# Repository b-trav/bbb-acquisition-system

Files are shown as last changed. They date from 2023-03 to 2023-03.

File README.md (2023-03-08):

# BEAGLEBONE BLACK ACQUISITION SYSTEM

__IMPORTANT: This project was last updated in 2017, so many commands and links are likely to be out of date.__

## Introduction

This project will show you how to create an 8 channel 24-bit 130 kSPS 
data acquisition system using a Beaglebone Black, four ADS1271 
Evaluation modules and a few other electronic bits and pieces.

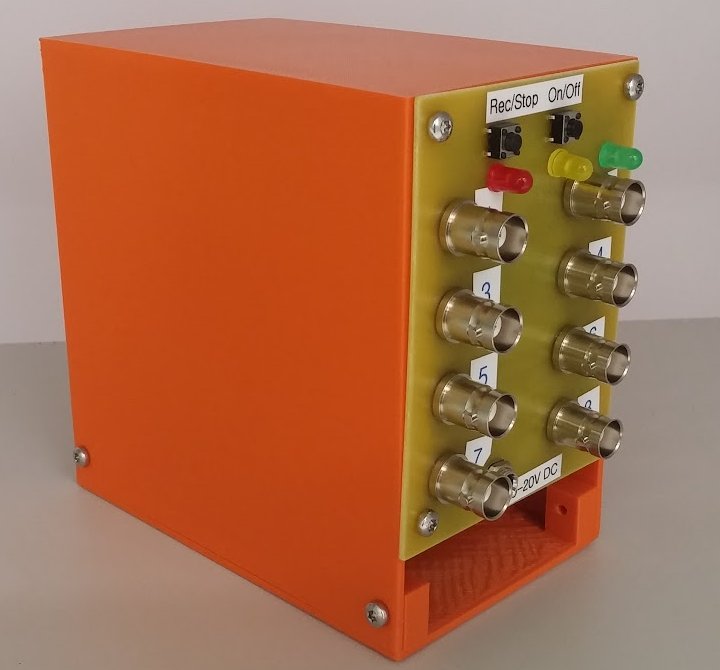
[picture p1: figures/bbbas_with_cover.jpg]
BBB Acquisition System with cover The BBB Acquisition System


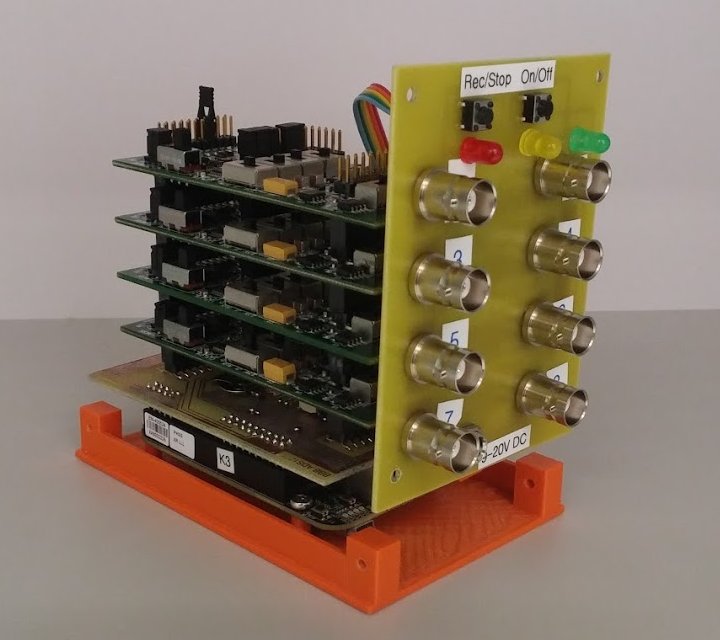
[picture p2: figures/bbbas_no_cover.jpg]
BBB Acquisition System without cover Inside the BBB Acquisition System


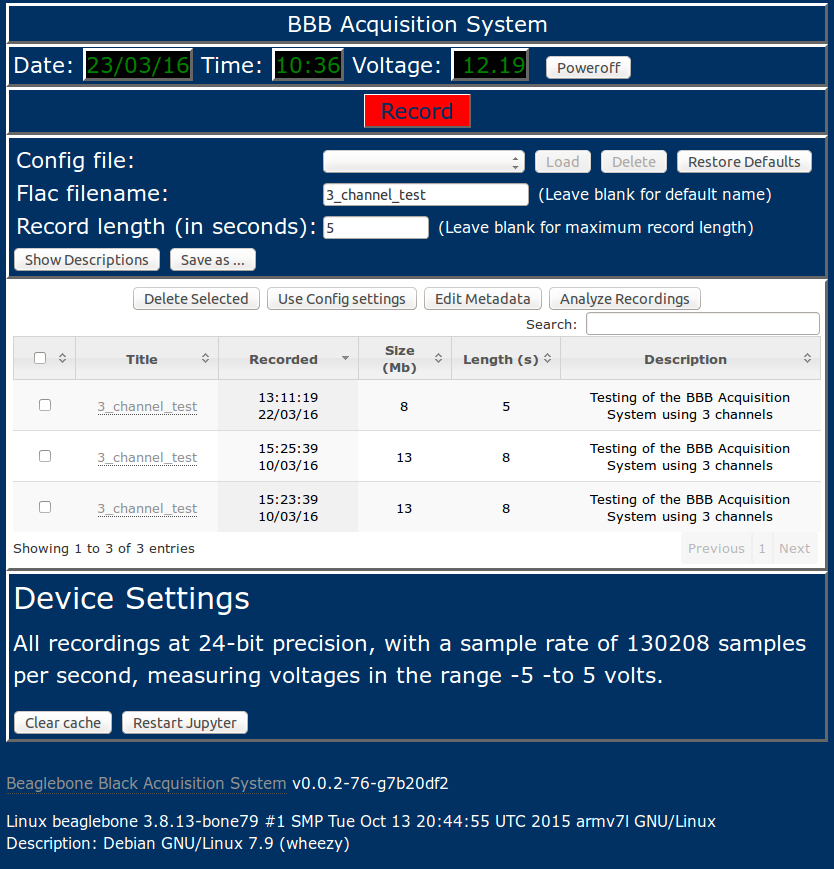
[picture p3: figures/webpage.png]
BBB Acquisition System webpage GUI interface of the BBB Acquisition System


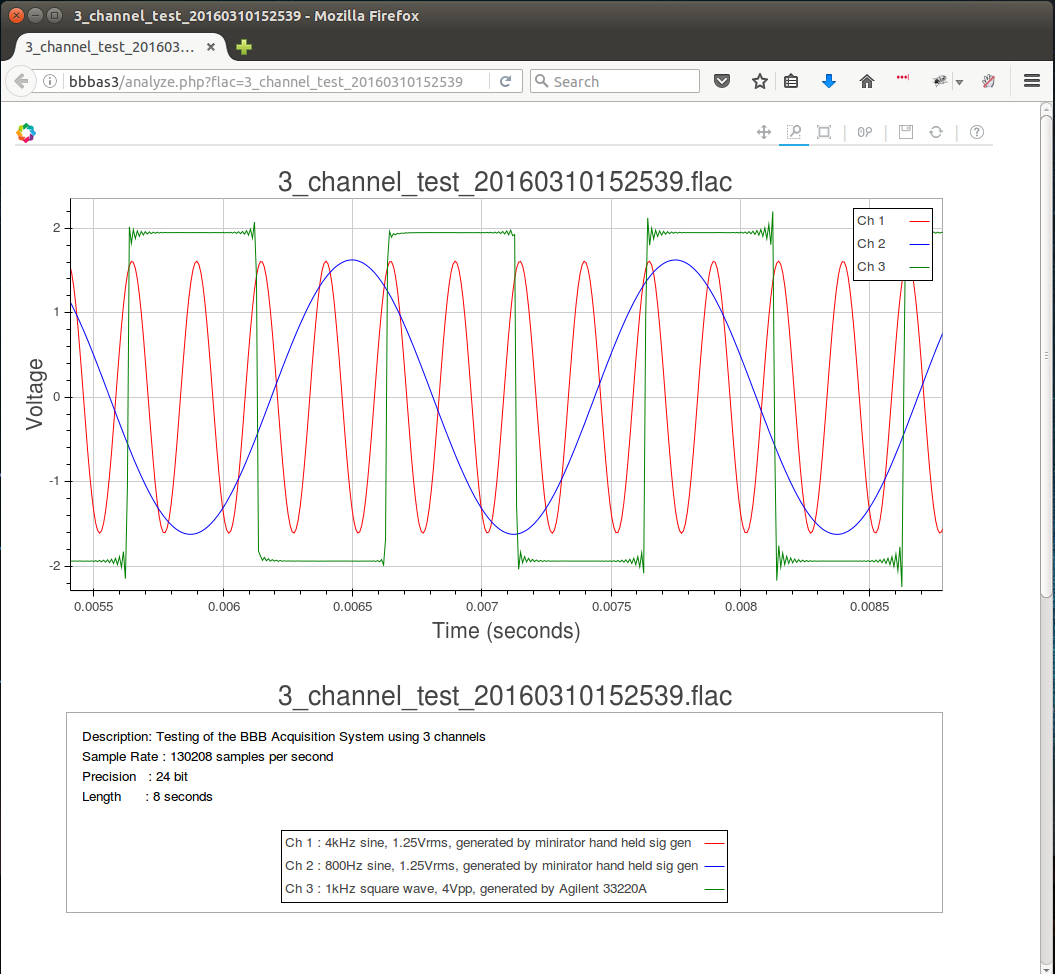
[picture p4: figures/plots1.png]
BBB Acquisition System Analysis Analysis of acquired data


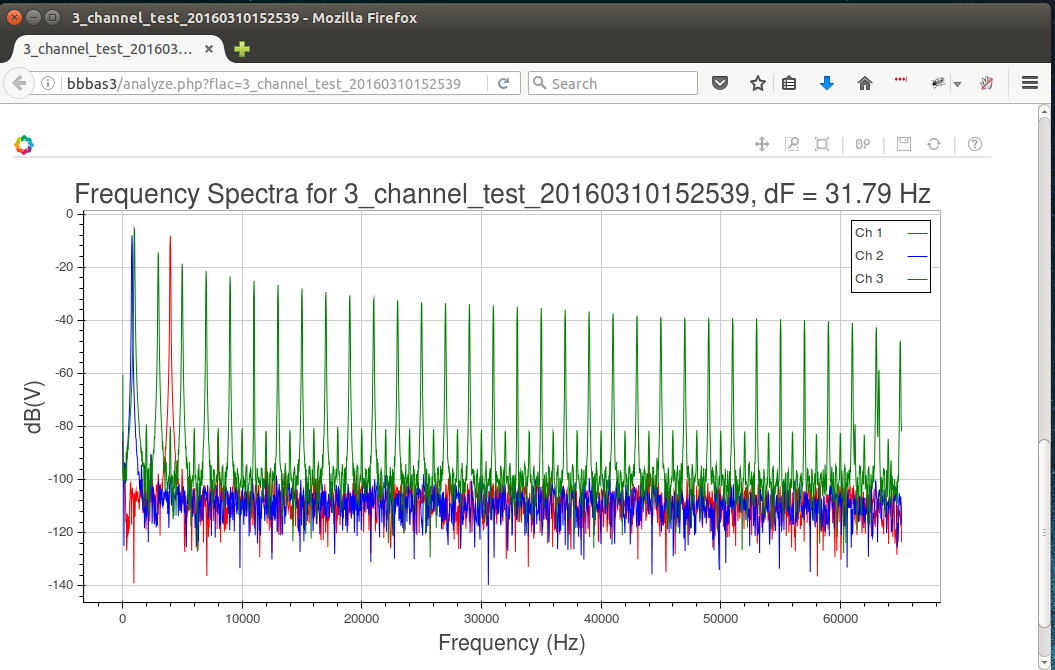
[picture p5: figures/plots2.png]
BBB Acquisition System Analysis Spectral analysis of acquired data


The aim of this project is to give people access to a reliable, 
high-precision data acquisition system which runs at a respectable 
sample rate without having to shell out tens of thousands of dollars.

## Client-side App

The acquisition system can be controlled with any browser, however, to check on the
progress of a recording, or look at the third octave levels of an input, it is necessary
to run a python script on the computer used to access the BBBAS.

To use the client-side app, you need to install python, as well as numpy and bokeh.
So far, the client-side app has only been tested in linux.
The client side app is run using the command
```
BBBASDIR=~/bbb-acquisition-system
bokeh serve --unused-session-lifetime 10 --port 5006 $BBBASDIR/source/third_octave_local.py $BBBASDIR/source/record_progress.py
``` 
This assumes that you have cloned the bbb-acquisition-system repository into
your home directory.

## Bill of Materials

| Product | (Approx.) Price<sup>1</sup> (US$) |
|---------|----------------------------------:|
| [Beaglebone Black]                                          |  $55 |
| [ADS1271EVM] ( 4 @ $49 )                                    | $196 |
| [12V 2A DC Power Supply]<sup>2</sup>                        |   $4 |
| [2Gb microSD card]<sup>3</sup>                              |   $2 |
| [larger microSD card]<sup>4</sup>                           |   $4 |
| [BBB_ADS1271 Cape](#Cape)                                   |  $80 |
| [BBB ADS1271 Front Panel](#FrontPanel)                      |  $30 |
| [Wifi dongle] (optional)                                    |  $12 |
| __Case (optional)__ 
| [Base](#Base) (27 cm<sup>3</sup> of plastic)                |  $10 |
| [Cover](#Cover) (91 cm<sup>3</sup> of plastic)              |  $25 |
| __TOTAL__                                               | __$418__ |

[Beaglebone Black]:http://beagleboard.org/BLACK
[ADS1271EVM]: http://www.ti.com/tool/ads1271evm
[12V 2A DC Power Supply]: http://www.ebay.com/sch/12v+2a+power+supply
[2Gb microSD card]: http://www.ebay.com/sch/2Gb+micro+SD+card
[larger microSD card]: http://www.ebay.com/sch/micro+SD+card
[Wifi dongle]: https://www.adafruit.com/products/814
__Footnotes__:
 
<sup>1</sup>Some components will need to be purchased in quantities 
greater than those required by a single acquisition system, leading to 
a larger over-all cost for the creation of a single unit.

<sup>2</sup>The device will run with any supply voltage between 10 and 
20 volts.

<sup>3</sup>For storing the Linux Debian operating system flasher 
(Can be larger than 2Gb).

<sup>4</sup>For storing the acquired data.

## Software installation procedure

* Download the following compressed flasher image of the debian operating system 
  for the beaglebone black. 
  * [kernel: 3.8.13-bone79 Debian Wheezy image](https://rcn-ee.com/rootfs/bb.org/release/2015-11-03/console/BBB-eMMC-flasher-debian-7.9-console-armhf-2015-11-03-2gb.img.xz)

  > ### Background
  > 
  > There are a heap of different kernel versions of debian available 
  > to download,
  > thanks to the good work of [RobertCNelson](https://github.com/RobertCNelson).
  > These images can be found on the [Embedded Linux Wiki](http://elinux.org/Beagleboard:BeagleBoneBlack_Debian).
  > 
  > I am far from an expert in the world of linux or embedded systems, 
  > but as I understand it, there are two main distinctions with the 
  > kernels.
  > There are kernels 8.13.x which have good support for the 
  > capemanager, but are now rather old, and
  > then there are newer kernels which have better reliability with 
  > regard to wifi etc, but do not *yet* provide good support for adding 
  > capes or using the PRUs.
  > 
  > I have attempted to create an ADS1271 cape which works with 
  > newer kernels, but I have run into some issues. If you are adventurous,
  > you can try:
  > * [kernel: 4.1.16-ti-rt-r44 Debian Jessie image](https://rcn-ee.com/rootfs/bb.org/testing/2016-01-31/console/BBB-eMMC-flasher-debian-8.3-console-armhf-2016-01-31-2gb.img.xz)
  > 
  > CURRENT BUGS: 
  >   * Boot freezes for several minutes when wifi dongle is attached
  >   * Boot freezes for several minutes when PRU is enabled

* Copy this image onto a 2Gb microSD card (this is the minimum size – a 
  larger microSD card will work fine)

  * **Linux** :
  Follow [these instructions](http://www.ev3dev.org/docs/tutorials/writing-sd-card-image-linux-command-line/)

  * **Windows** :
  Follow [these instructions](https://learn.adafruit.com/beaglebone-black-installing-operating-systems/windows)

  * **Mac** :
  Follow [these instructions](https://learn.adafruit.com/beaglebone-black-installing-operating-systems/mac-os-x)

* Eject and insert the SD card into the BBB and power it up (you may need to hold down the SD card
  button on the BBB). 
  Wait for the image to be flashed to the emmc (takes a few minutes) while it is processing, the blues leds should be sweeping back and forth. On conclusion all the blue leds should be on (or wait another minute or so and the device should have powered itself down). 

* Remove the microSD card from the BBB, and save it in case you need to start the installation procedure again, or create another device. 

* **IMPORTANT!!!** LABEL the microSD card CLEARLY, as inserting this into a BBB and powering the device will wipe the eMMC on the beaglebone black.

* Insert a blank (fat32 formatted) microSD card into the BBB. 

* Power up the BBB by connecting the BBB to a computer via mini-USB. 

* WAIT a few minutes or so (be patient). NB: Probably best not to have the wifi
  dongle plugged in at this point.

* You should be able to connect to your beaglebone black.

* In order to connect to the beaglebone and get internet access, you need to do the following
on your computer:

  * **Linux** :
  
	Open a terminal, and type:

  ```
  sudo su
  ifconfig -a
  # Find out which connection the BBB is on (generally eth3, eth4, etc)
  # and which connection your internet is using (generally wlan0 etc)
  # in this example, the BBB is on eth5 and my internet is on wlan0
  ifconfig eth5 192.168.7.1
  iptables --table nat --append POSTROUTING --out-interface wlan0 -j MASQUERADE
  iptables --append FORWARD --in-interface eth5 -j ACCEPT
  echo 1 > /proc/sys/net/ipv4/ip_forward
  exit
  ssh debian@192.168.7.2
  ```

  * **Windows** : 
   
	Follow [these instructions](https://learn.adafruit.com/ssh-to-beaglebone-black-over-usb/installing-drivers-windows), and then [these instructions](https://learn.adafruit.com/ssh-to-beaglebone-black-over-usb/ssh-with-windows-and-putty).

  * **Mac** : 
   
	Follow [these instructions](https://learn.adafruit.com/ssh-to-beaglebone-black-over-usb/installing-drivers-mac), and then open a terminal and type:
  
  ```
  ssh debian@192.168.7.2
  ```

* Once you have ssh access to the beaglebone, log in via ssh (the default password is temppwd) and then type:

  ```
  sudo ip route add default via 192.168.7.1
  sudo sh -c "echo 'nameserver 8.8.8.8' >> /etc/resolv.conf"
  sudo apt-get -y update
  sudo apt-get -y install git locales
  sudo dpkg-reconfigure locales
  sudo dpkg-reconfigure tzdata
  sudo sh -c "locale > /etc/locale.conf"
  git clone https://github.com/bbb-acquisition-system
  sudo bbb-acquisition-system/install.sh  2>&1 | tee install-bbb-as-log.txt
  ```
  
  Unfortunately this installation procedure takes a reasonably long time 
  (depending on your internet access speed) 
  because we need to install quite a few applications.
  The main hold-up is a couple of python packages (numpy and jupyter),
  which take roughly 35 minutes and 15 minutes respectively to install.
  This gives a total install time of around an hour. 
  Assuming you've set up your locale and timezone, the only user inputs
  are a root password, and then some wifi info at the very end. 
  So after giving your root password,
  go take a long walk, and come back in around an hour.

* After re-booting the BBB you should be able to access your 
  Beaglebone Black Acquisition System by going
  to the ip address of the BBB using a browser of your choice. 

## Building the boards

The BBB Acquisition System requires two printed computer boards (PCBs) to function correctly.
The [Eagle](http://www.cadsoftusa.com/download-eagle/) schematics and 
boards are contained in the PCBs directory, this directory also contains
a set of gerber files for each board.
These boards can be produced using the PCB production company of your choice, or can be generated
in-house, assuming you have the relevant know-how.

### BBB ADS1271 Cape

This board provides power, a real-time clock and the connections between the BBB and
the ADS1271EVMs. 
[Here](PCBs/BBB_ADS1271_cape_parts.html) is a parts list for this board.
Some of the items can only be purchased in large quantities, such as the surface mounted LEDs.
These are not strictly necessary, so if you do not have access to some surface mounted LEDs,
then these can be omitted.

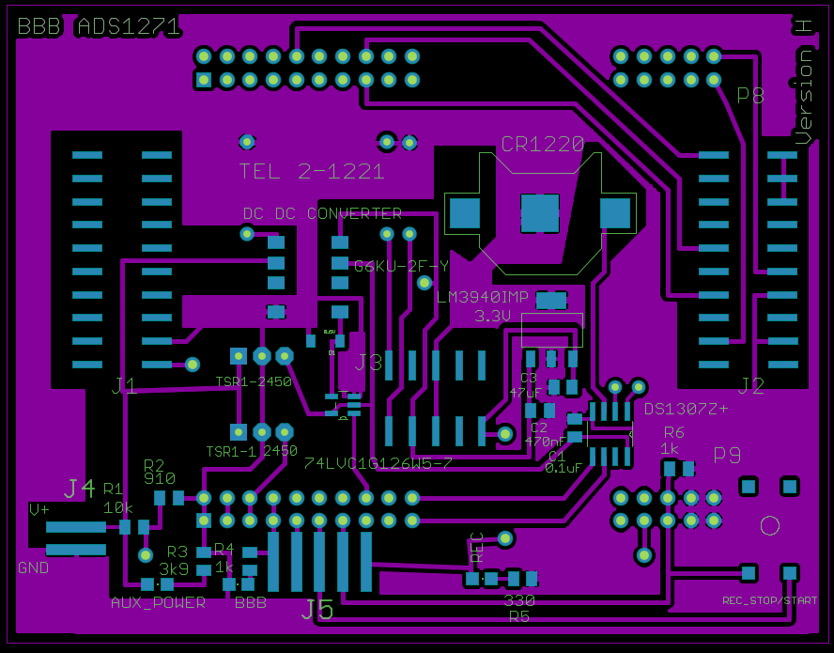
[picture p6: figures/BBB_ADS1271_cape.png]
BBB ADS1271 Cape Board diagram for the BBB ADS1271 Cape


### BBB ADS1271 Front Panel

This board provides the inputs to the system as well as on/off and recording lights and buttons.
[Here](PCBs/BBB_ADS1271_front_panel_parts.html) is a parts list for this board.

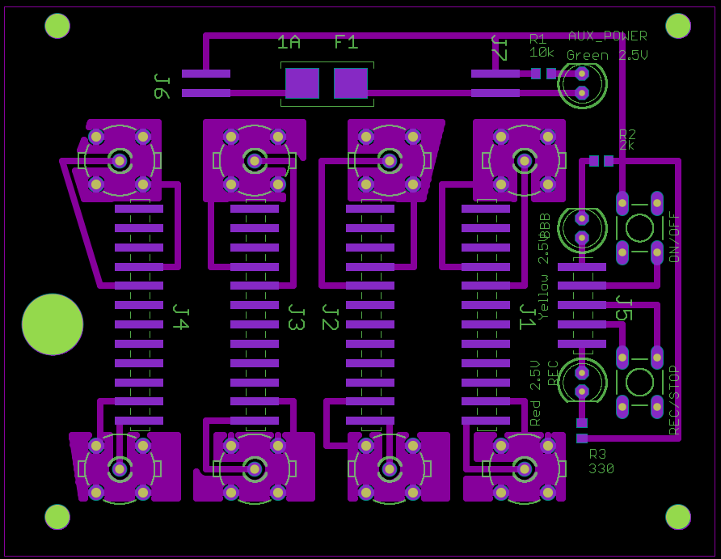
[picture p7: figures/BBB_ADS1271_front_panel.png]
BBB ADS1271 Front Panel Board diagram for the BBB ADS1271 Front Panel


## Building the case

The case for the unit is optional, although highly recommended.
The case directory contains the [blender](https://www.blender.org/) 
and [stl](https://en.wikipedia.org/wiki/STL_%28file_format%29) files for the case.
Once again, if you have access to a 3D printer, you can produce this yourself, otherwise
there are plenty of [3D printing companies](http://3dprintingpricecheck.com/) that you could use.

### Base

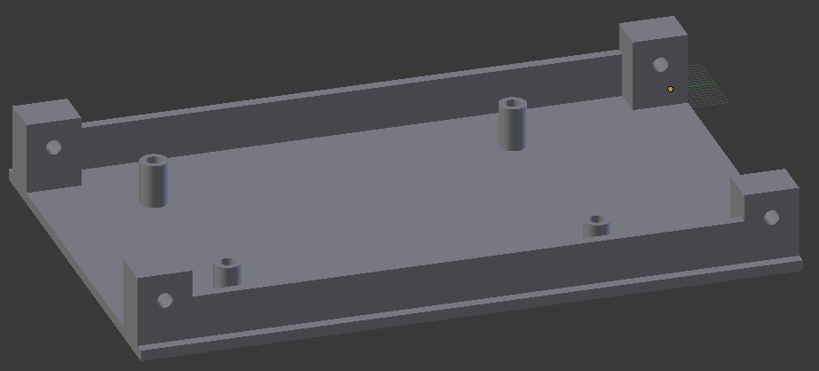
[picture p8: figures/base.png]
BBB Acquisition System Base Base for the BBB Acquisition System


### Cover

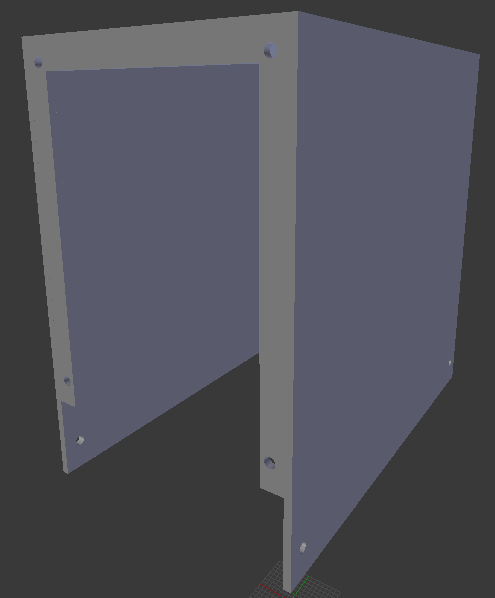
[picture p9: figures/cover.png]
BBB Acquisition System Cover Cover for the BBB Acquisition System


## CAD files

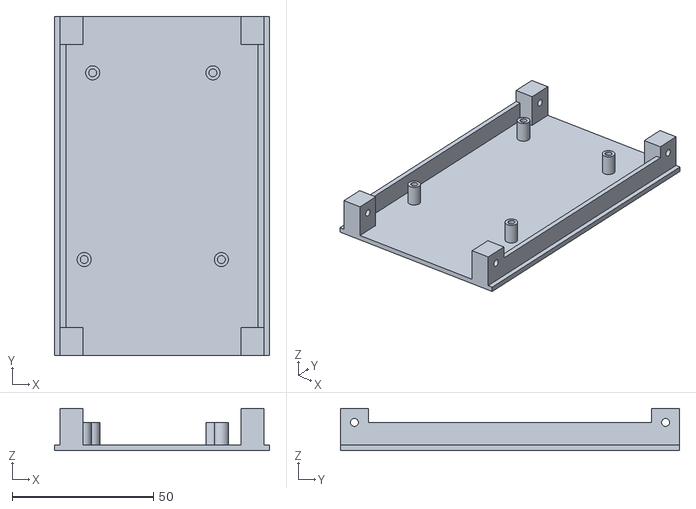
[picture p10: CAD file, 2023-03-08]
case/case_base.stl
76.0 x 120.0 x 15.0

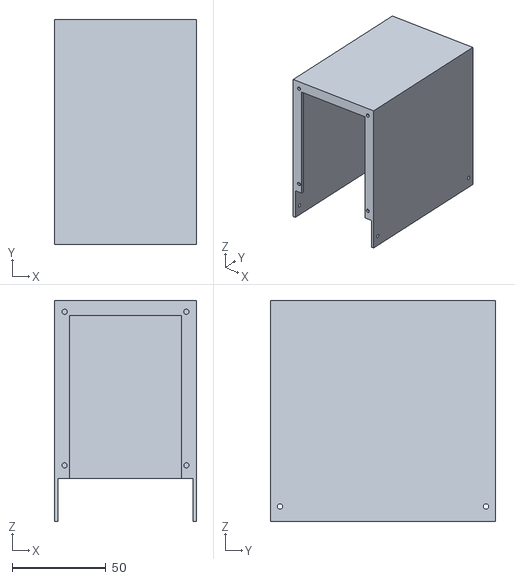
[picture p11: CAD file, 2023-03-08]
case/case_cover.stl
76.0 x 120.0 x 118.0

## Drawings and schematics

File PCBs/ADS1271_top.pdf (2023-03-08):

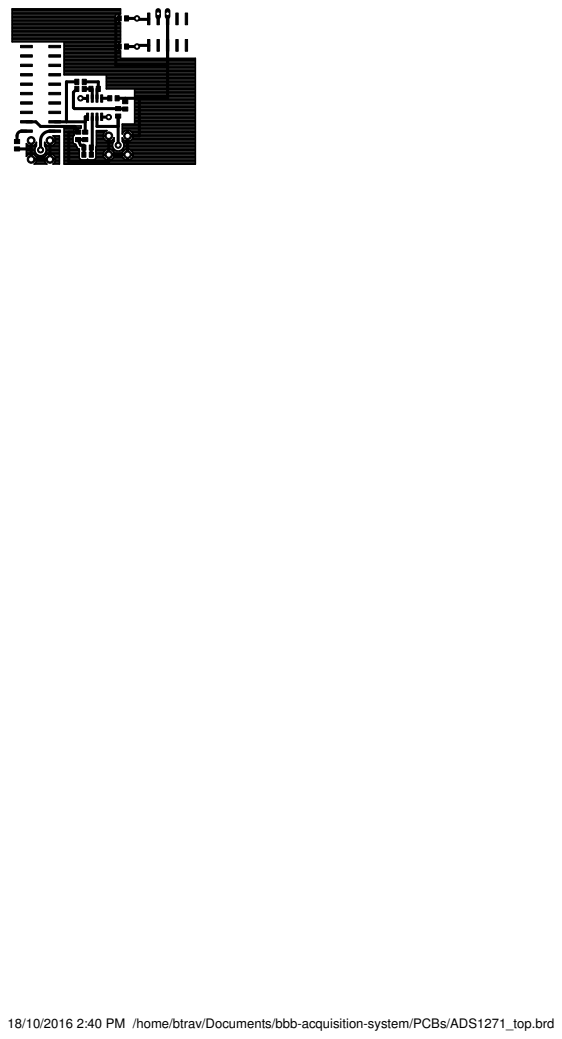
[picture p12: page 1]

18/10/2016 2:40 PM /home/btrav/Documents/bbb-acquisition-system/PCBs/ADS1271_top.brd

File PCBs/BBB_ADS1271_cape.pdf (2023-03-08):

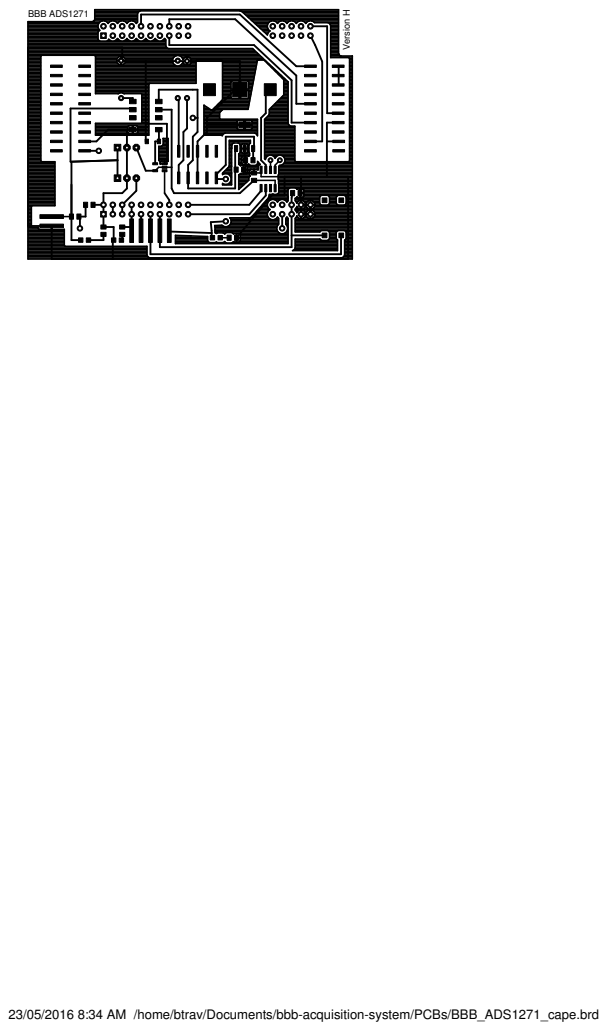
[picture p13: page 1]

23/05/2016 8:34 AM /home/btrav/Documents/bbb-acquisition-system/PCBs/BBB_ADS1271_cape.brd

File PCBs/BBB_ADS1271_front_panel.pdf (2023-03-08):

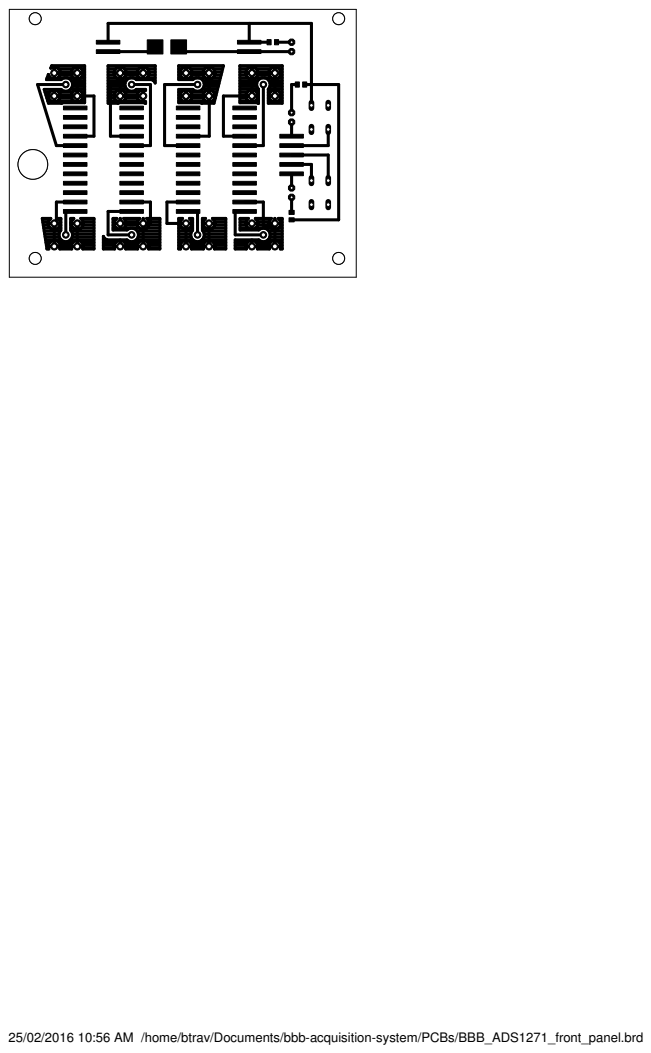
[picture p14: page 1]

25/02/2016 10:56 AM /home/btrav/Documents/bbb-acquisition-system/PCBs/BBB_ADS1271_front_panel.brd

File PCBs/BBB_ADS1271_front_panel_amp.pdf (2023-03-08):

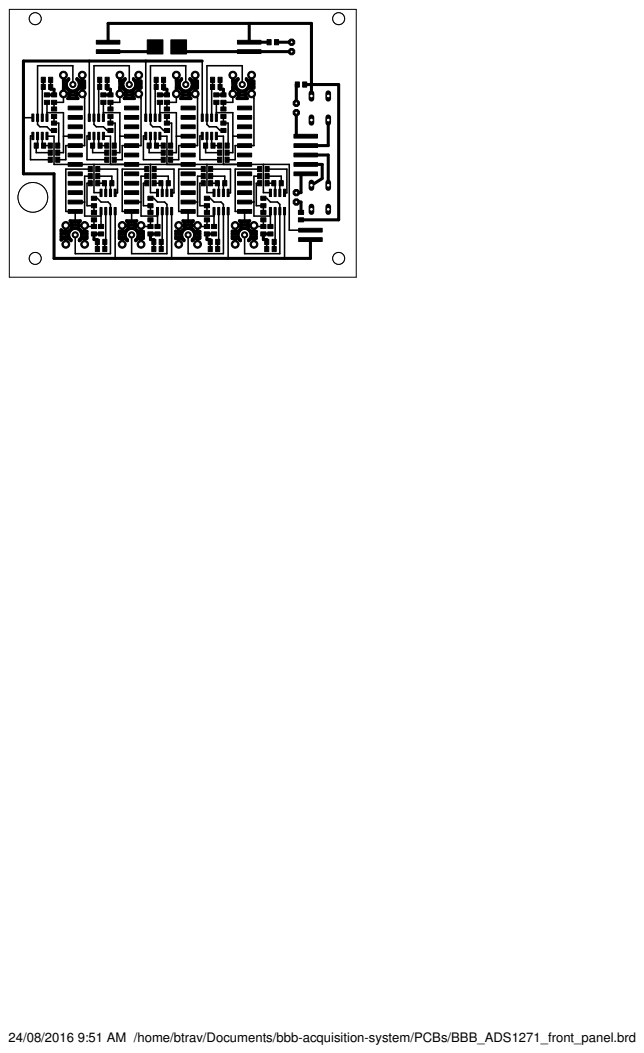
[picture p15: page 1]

24/08/2016 9:51 AM /home/btrav/Documents/bbb-acquisition-system/PCBs/BBB_ADS1271_front_panel.brd

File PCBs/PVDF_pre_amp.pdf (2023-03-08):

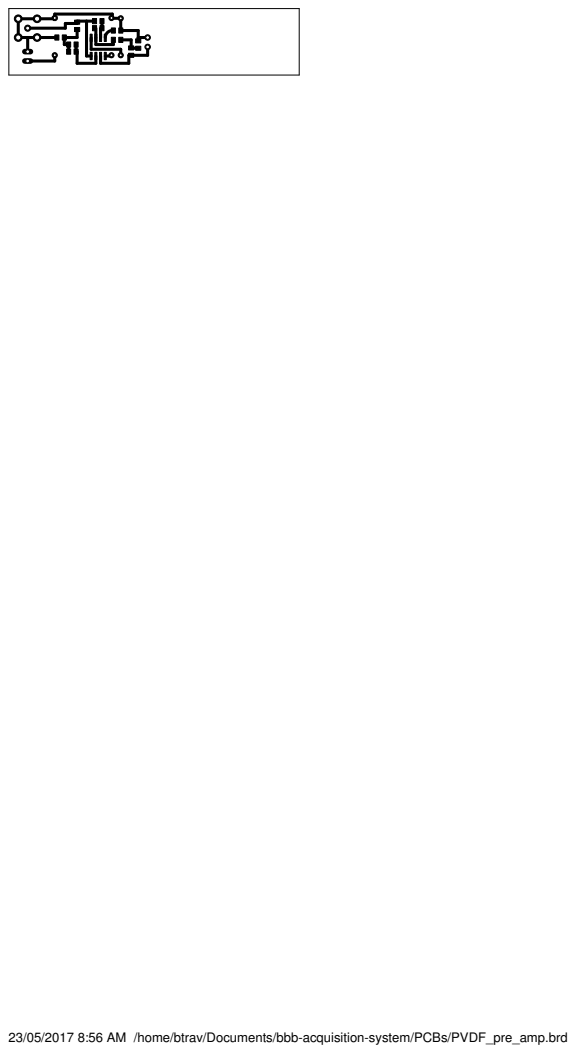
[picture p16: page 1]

23/05/2017 8:56 AM /home/btrav/Documents/bbb-acquisition-system/PCBs/PVDF_pre_amp.brd

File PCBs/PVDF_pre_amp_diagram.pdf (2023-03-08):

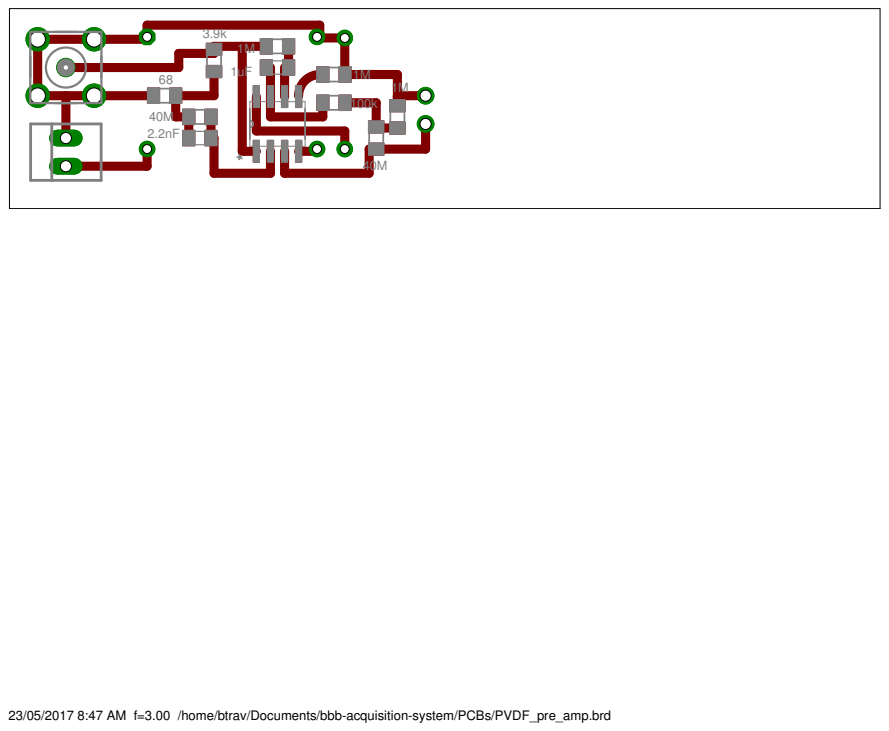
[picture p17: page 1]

23/05/2017 8:47 AM f=3.00 /home/btrav/Documents/bbb-acquisition-system/PCBs/PVDF_pre_amp.brd

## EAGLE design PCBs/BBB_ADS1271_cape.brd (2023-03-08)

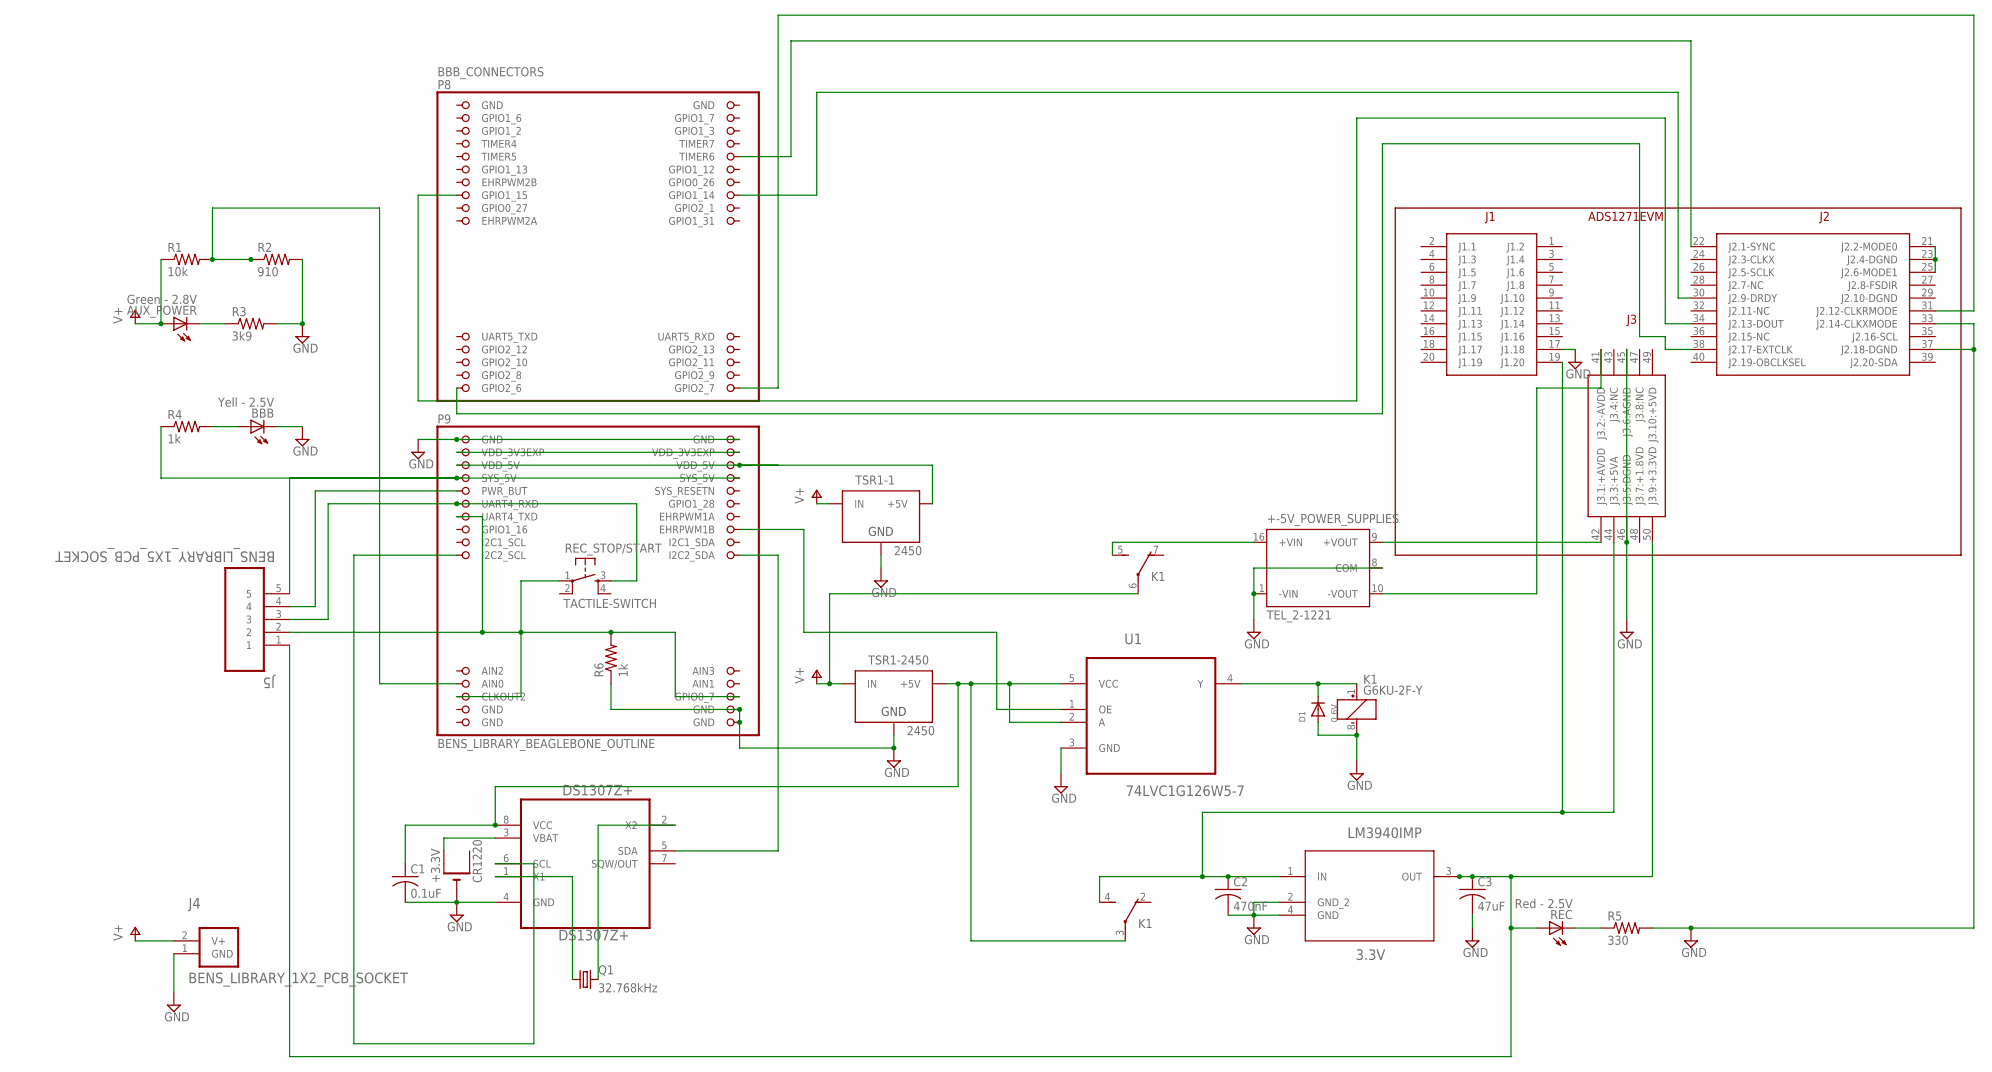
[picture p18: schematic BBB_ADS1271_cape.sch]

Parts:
+-5V_POWER_SUPPLIES: TEL_2-1221; TRACOPOWER2W
ADS1271_CONNECTORS: BENS_LIBRARY_ADS1271EVM
AUX_POWER: Green - 2.8V; CHIPLED_0805
BBB: Yell - 2.5V; CHIPLED_0805
BBB_CONNECTORS: BENS_LIBRARY_BEAGLEBONE_OUTLINE; BENS_LIBRARY_BEAGLEBONE_SHIELD
C1: 0.1uF; C0805K
C2: 470nF; C0805K
C3: 47uF; C0805K
CR1220: +3.3V; ADAFRUIT_CR1220-SMD
D1: 0.6V; SOD-123FL
DS1307Z+: DS1307Z+; MAXIM_BY_ELEMENT14_BATCH_1_SOIC127P600X175-8N
J4: BENS_LIBRARY_1X2_PCB_SOCKET
J5: BENS_LIBRARY_1X5_PCB_SOCKET; BENS_LIBRARY_SAMTEC_SSM-15-L-DV-BE
K1: G6KU-2F-Y
LM3940IMP: 3.3V; NSC_BY_ELEMENT14_BATCH_1.1_SOT230P696X180-4N
Q1: 32.768kHz; TC38H
R1: 10k; ADAFRUIT_R0805
R2: 910; ADAFRUIT_R0805
R3: 3k9; ADAFRUIT_R0805
R4, R6: 1k; ADAFRUIT_R0805
R5: 330; ADAFRUIT_R0805
REC: Red - 2.5V; CHIPLED_0805
REC_STOP/START: TACTILE-SWITCH; 7914G-6MM
TSR1-1, TSR1-2450: 2450; STEELCAVEROBOTICS-POWER_TSR-1
U1: 74LVC1G126W5-7; SOT95P280X145-5N

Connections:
3.3V_BBB_1: BBB_CONNECTORS.57 (UART4_RXD), J5.3, REC_STOP/START.3
3.3V_BBB_2: ADS1271_CONNECTORS.31 (J2.12-CLKRMODE), BBB_CONNECTORS.46 (GPIO2_7)
3.3V_RELAY: ADS1271_CONNECTORS.50 (J3.9:+3.3VD), C3.1, J5.1, LM3940IMP.3 (OUT), REC.A
5V: C1.1, DS1307Z+.8 (VCC), K1.3, TSR1-2450.3 (+5V), U1.2 (A), U1.5 (VCC)
5V_BBB: BBB_CONNECTORS.51 (VDD_5V), BBB_CONNECTORS.52 (VDD_5V), TSR1-1.3 (+5V)
5V_RELAY: ADS1271_CONNECTORS.19 (J1.20), ADS1271_CONNECTORS.44 (J3.3:+5VA), C2.1, K1.4 (S), LM3940IMP.1 (IN)
+5V_OP_AMP: +-5V_POWER_SUPPLIES.9 (+VOUT), ADS1271_CONNECTORS.42 (J3.1:+AVDD)
-5V_OP_AMP: +-5V_POWER_SUPPLIES.10 (-VOUT), ADS1271_CONNECTORS.41 (J3.2:-AVDD)
CLK: ADS1271_CONNECTORS.38 (J2.17-EXTCLK), BBB_CONNECTORS.45 (GPIO2_6)
DGND: ADS1271_CONNECTORS.21 (J2.2-MODE0), ADS1271_CONNECTORS.23 (J2.4-DGND), ADS1271_CONNECTORS.25 (J2.6-MODE1)
DOUT: ADS1271_CONNECTORS.34 (J2.13-DOUT), BBB_CONNECTORS.15 (GPIO1_15)
DRDY: ADS1271_CONNECTORS.30 (J2.9-DRDY), BBB_CONNECTORS.16 (GPIO1_14)
GND: +-5V_POWER_SUPPLIES.1 (-VIN), +-5V_POWER_SUPPLIES.8 (COM), ADS1271_CONNECTORS.17 (J1.18), ADS1271_CONNECTORS.33 (J2.14-CLKXMODE), ADS1271_CONNECTORS.37 (J2.18-DGND), ADS1271_CONNECTORS.45 (J3.6:AGND), ADS1271_CONNECTORS.46 (J3.5:DGND), BBB.C, BBB_CONNECTORS.47 (GND), BBB_CONNECTORS.48 (GND), BBB_CONNECTORS.89 (GND), BBB_CONNECTORS.90 (GND), BBB_CONNECTORS.91 (GND), BBB_CONNECTORS.92 (GND), C1.2, C2.2, C3.2, CR1220.-, D1.A, DS1307Z+.4 (GND), J4.1 (GND), K1.8 (-), LM3940IMP.2 (GND_2), LM3940IMP.4 (GND), R2.2, R3.2, R5.2, R6.1, TSR1-1.2 (GND), TSR1-2450.2 (GND), U1.3 (GND)
unnamed: CR1220.+$2 (+1), DS1307Z+.3 (VBAT)
unnamed: +-5V_POWER_SUPPLIES.16 (+VIN), K1.5 (S)
unnamed: BBB_CONNECTORS.85 (AIN0), R1.2, R2.1
unnamed: BBB_CONNECTORS.66 (I2C2_SDA), DS1307Z+.5 (SDA)
unnamed: BBB_CONNECTORS.65 (I2C2_SCL), DS1307Z+.6 (SCL)
unnamed: DS1307Z+.2 (X2), Q1.2
unnamed: DS1307Z+.1 (X1), Q1.1
unnamed: AUX_POWER.C, R3.1
unnamed: D1.C, K1.1 (+), U1.4 (Y)
unnamed: R5.1, REC.C
unnamed: BBB.A, R4.2
P8.9: BBB_CONNECTORS.62 (EHRPWM1B), U1.1 (OE)
PWR_BUT: BBB_CONNECTORS.55 (PWR_BUT), J5.4
REC_SWITCH: BBB_CONNECTORS.59 (UART4_TXD), BBB_CONNECTORS.87 (CLKOUT2), BBB_CONNECTORS.88 (GPIO0_7), J5.2, R6.2, REC_STOP/START.1
SYNC: ADS1271_CONNECTORS.22 (J2.1-SYNC), BBB_CONNECTORS.10 (TIMER6)
SYS_5V: BBB_CONNECTORS.53 (SYS_5V), BBB_CONNECTORS.54 (SYS_5V), J5.5, R4.1
V+: AUX_POWER.A, J4.2 (V+), K1.6, R1.1, TSR1-1.1 (IN), TSR1-2450.1 (IN)
VDD_3V3EXP: BBB_CONNECTORS.49 (VDD_3V3EXP), BBB_CONNECTORS.50 (VDD_3V3EXP)

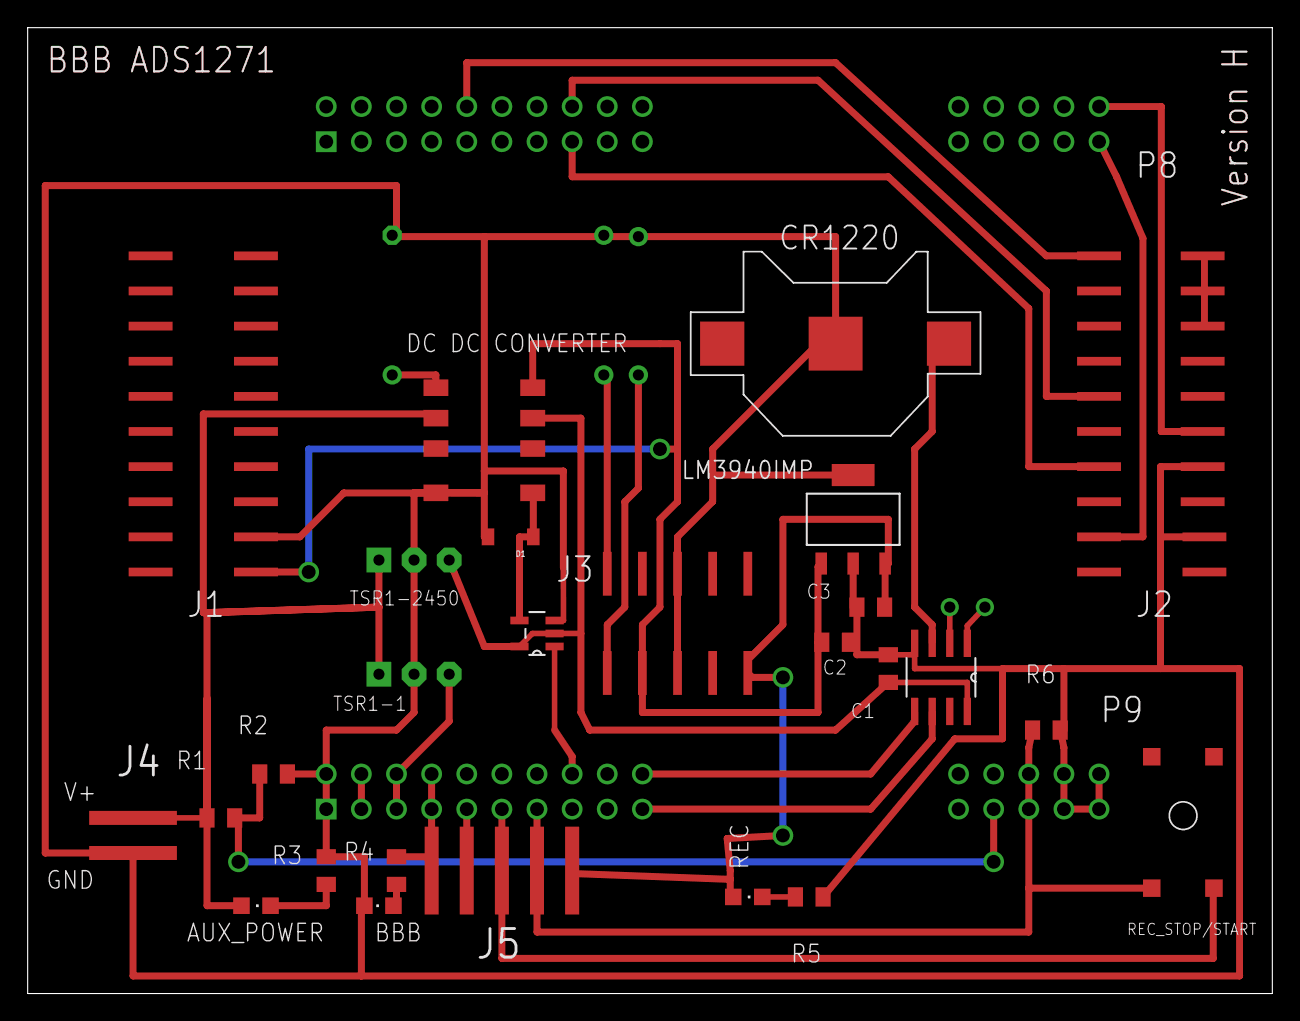
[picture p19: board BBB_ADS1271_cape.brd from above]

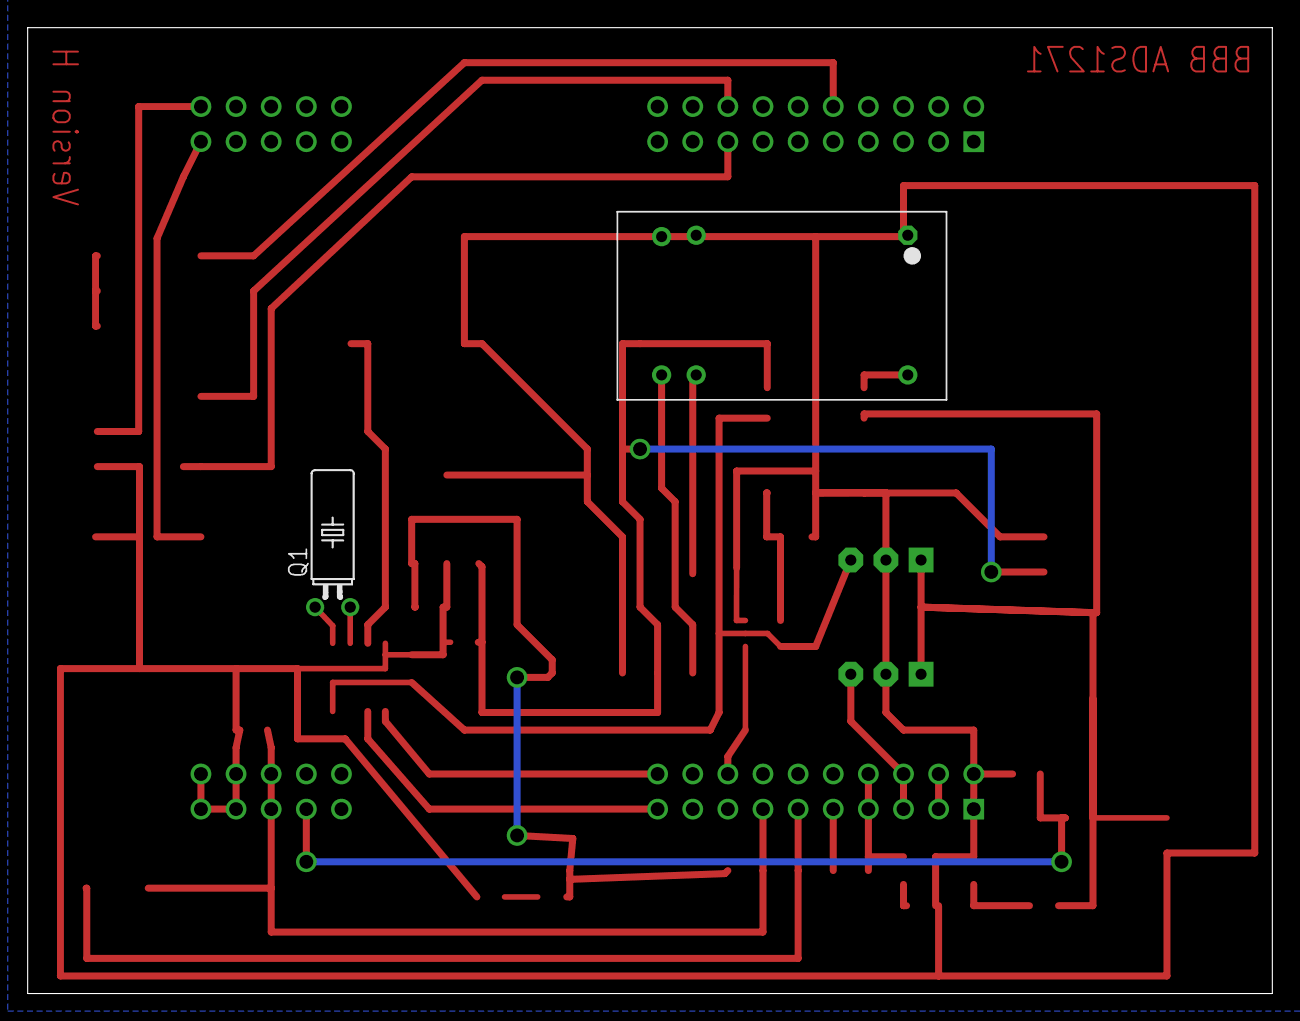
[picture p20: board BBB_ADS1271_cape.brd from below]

Board: 2 copper layers, 90.0 x 69.8 mm, 27 parts (4 on the bottom side), 31 nets.

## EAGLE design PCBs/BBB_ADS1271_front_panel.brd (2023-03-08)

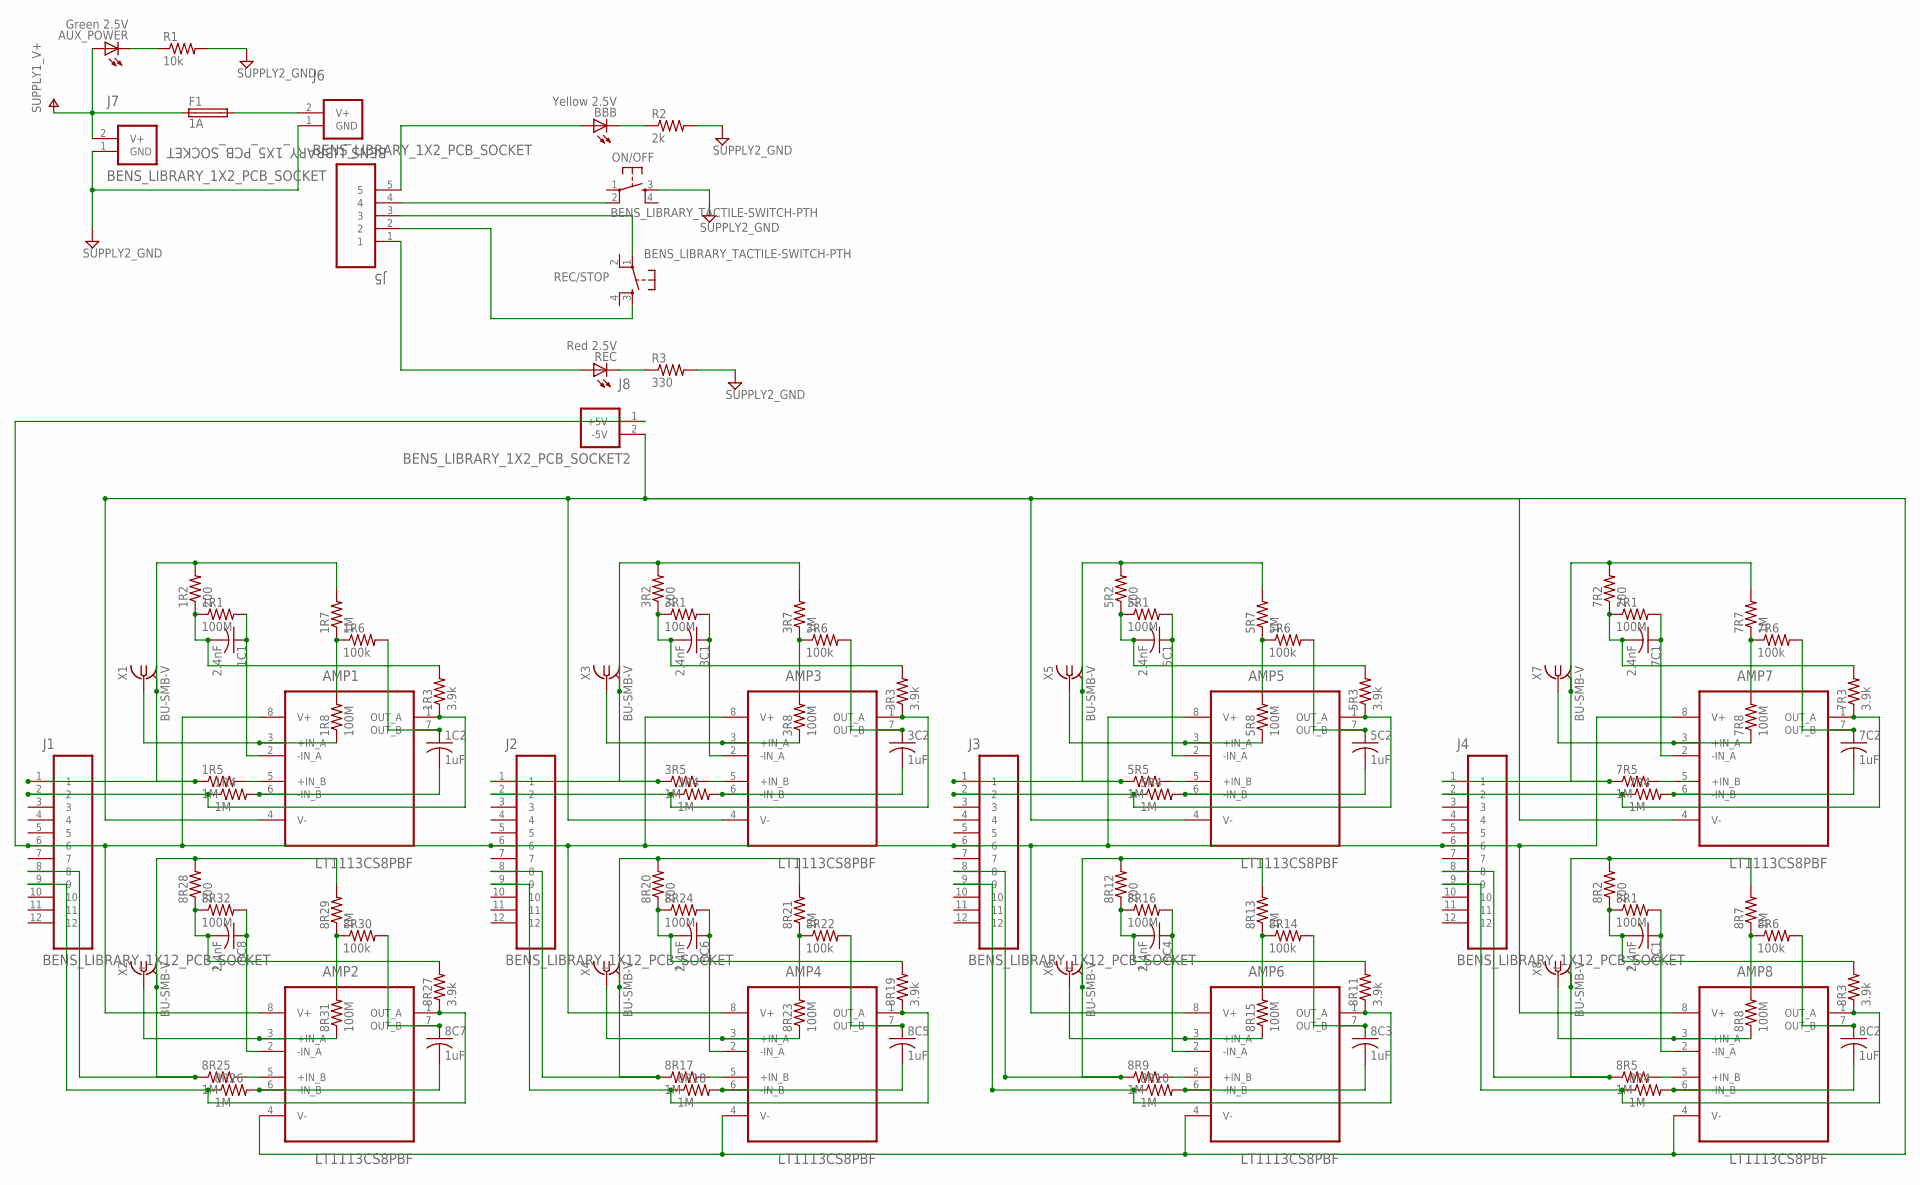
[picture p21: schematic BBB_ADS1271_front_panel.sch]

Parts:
1C1, 3C1, 5C1, 7C1, 8C1, 8C4, 8C6, 8C8: 2.4nF; ADAFRUIT_C0805K
1C2, 3C2, 5C2, 7C2, 8C2, 8C3, 8C5, 8C7: 1uF; ADAFRUIT_C0805K
1R1, 1R8, 3R1, 3R8, 5R1, 5R8, 7R1, 7R8, 8R1, 8R8, 8R15, 8R16, 8R23, 8R24, 8R31, 8R32: 100M; ADAFRUIT_R0805
1R2, 3R2, 5R2, 7R2, 8R2, 8R12, 8R20, 8R28: 200; ADAFRUIT_R0805
1R3, 3R3, 5R3, 7R3, 8R3, 8R11, 8R19, 8R27: 3.9k; ADAFRUIT_R0805
1R4, 1R5, 1R7, 3R4, 3R5, 3R7, 5R4, 5R5, 5R7, 7R4, 7R5, 7R7, 8R4, 8R5, 8R7, 8R9, 8R10, 8R13, 8R17, 8R18, 8R21, 8R25, 8R26, 8R29: 1M; ADAFRUIT_R0805
1R6, 3R6, 5R6, 7R6, 8R6, 8R14, 8R22, 8R30: 100k; ADAFRUIT_R0805
AMP1, AMP2, AMP3, AMP4, AMP5, AMP6, AMP7, AMP8: LT1113CS8PBF; SOIC127P600X175-8N
AUX_POWER: Green 2.5V; ADAFRUIT_LED5MM
BBB: Yellow 2.5V; ADAFRUIT_LED5MM
F1: 1A; LITTLEFUSE_PACKAGE
J1, J2, J3, J4: BENS_LIBRARY_1X12_PCB_SOCKET; BENS_LIBRARY_SAMTEC_SSM-112-L-DV-BE
J5: BENS_LIBRARY_1X5_PCB_SOCKET; BENS_LIBRARY_SAMTEC_SSM-15-L-DV-BE
J6, J7: BENS_LIBRARY_1X2_PCB_SOCKET
J8: BENS_LIBRARY_1X2_PCB_SOCKET2
ON/OFF: BENS_LIBRARY_TACTILE-SWITCH-PTH; BENS_LIBRARY_TAC-SWITCH-PTH
R1: 10k; ADAFRUIT_R0805
R2: 2k; ADAFRUIT_R0805
R3: 330; ADAFRUIT_R0805
REC: Red 2.5V; ADAFRUIT_LED5MM
REC/STOP: BENS_LIBRARY_TACTILE-SWITCH-PTH; BENS_LIBRARY_TAC-SWITCH-PTH
X1, X2, X3, X4, X5, X6, X7, X8: BU-SMB-V

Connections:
1+IN_B: 1R5.2, AMP1.5 (+IN_B)
1-IN_A: 1C1.1, 1R1.2, AMP1.2 (-IN_A)
1-IN_B: 1C2.2, 1R4.2, AMP1.6 (-IN_B)
1OUT_B: 1C2.1, 1R6.2, AMP1.7 (OUT_B)
1W1: 1C1.2, 1R1.1, 1R2.1, 1R3.2
1W2: 1R6.1, 1R7.1, 1R8.2
2+IN_B: 8R25.2, AMP2.5 (+IN_B)
2-IN_A: 8C8.1, 8R32.2, AMP2.2 (-IN_A)
2-IN_B: 8C7.2, 8R26.2, AMP2.6 (-IN_B)
2OUT_B: 8C7.1, 8R30.2, AMP2.7 (OUT_B)
2W1: 8C8.2, 8R27.2, 8R28.1, 8R32.1
2W2: 8R29.1, 8R30.1, 8R31.2
3+IN_B: 3R5.2, AMP3.5 (+IN_B)
3-IN_A: 3C1.1, 3R1.2, AMP3.2 (-IN_A)
3-IN_B: 3C2.2, 3R4.2, AMP3.6 (-IN_B)
3OUT_B: 3C2.1, 3R6.2, AMP3.7 (OUT_B)
3W1: 3C1.2, 3R1.1, 3R2.1, 3R3.2
3W2: 3R6.1, 3R7.1, 3R8.2
4+IN_B: 8R17.2, AMP4.5 (+IN_B)
4-IN_A: 8C6.1, 8R24.2, AMP4.2 (-IN_A)
4-IN_B: 8C5.2, 8R18.2, AMP4.6 (-IN_B)
4OUT_B: 8C5.1, 8R22.2, AMP4.7 (OUT_B)
4W1: 8C6.2, 8R19.2, 8R20.1, 8R24.1
4W2: 8R21.1, 8R22.1, 8R23.2
5+IN_B: 5R5.2, AMP5.5 (+IN_B)
5-IN_A: 5C1.1, 5R1.2, AMP5.2 (-IN_A)
5-IN_B: 5C2.2, 5R4.2, AMP5.6 (-IN_B)
5OUT_B: 5C2.1, 5R6.2, AMP5.7 (OUT_B)
5W1: 5C1.2, 5R1.1, 5R2.1, 5R3.2
5W2: 5R6.1, 5R7.1, 5R8.2
6+IN_B: 8R9.2, AMP6.5 (+IN_B)
6-IN_A: 8C4.1, 8R16.2, AMP6.2 (-IN_A)
6-IN_B: 8C3.2, 8R10.2, AMP6.6 (-IN_B)
6OUT_B: 8C3.1, 8R14.2, AMP6.7 (OUT_B)
6W1: 8C4.2, 8R11.2, 8R12.1, 8R16.1
6W2: 8R13.1, 8R14.1, 8R15.2
7+IN_B: 7R5.2, AMP7.5 (+IN_B)
7-IN_A: 7C1.1, 7R1.2, AMP7.2 (-IN_A)
7-IN_B: 7C2.2, 7R4.2, AMP7.6 (-IN_B)
7OUT_B: 7C2.1, 7R6.2, AMP7.7 (OUT_B)
7W1: 7C1.2, 7R1.1, 7R2.1, 7R3.2
7W2: 7R6.1, 7R7.1, 7R8.2
8+IN_B: 8R5.2, AMP8.5 (+IN_B)
8-IN_A: 8C1.1, 8R1.2, AMP8.2 (-IN_A)
8-IN_B: 8C2.2, 8R4.2, AMP8.6 (-IN_B)
8OUT_B: 8C2.1, 8R6.2, AMP8.7 (OUT_B)
8W1: 8C1.2, 8R1.1, 8R2.1, 8R3.2
8W2: 8R6.1, 8R7.1, 8R8.2
+5V: AMP1.8 (V+), AMP2.8 (V+), AMP3.8 (V+), AMP4.8 (V+), AMP5.8 (V+), AMP6.8 (V+), AMP7.8 (V+), AMP8.8 (V+), J1.6, J2.6, J3.6, J4.6, J8.1 (+5V)
-5V: AMP1.4 (V-), AMP2.4 (V-), AMP3.4 (V-), AMP4.4 (V-), AMP5.4 (V-), AMP6.4 (V-), AMP7.4 (V-), AMP8.4 (V-), J8.2 (-5V)
ADC1_NEG: 1R3.1, 1R4.1, AMP1.1 (OUT_A), J1.2
ADC1_POS: 1R2.2, 1R5.1, 1R7.2, J1.1, X1.2, X1.3 (2), X1.4 (2), X1.5 (2)
ADC2_NEG: 8R26.1, 8R27.1, AMP2.1 (OUT_A), J1.9
ADC2_POS: 8R25.1, 8R28.2, 8R29.2, J1.8, X2.2, X2.3 (2), X2.4 (2), X2.5 (2)
ADC3_NEG: 3R3.1, 3R4.1, AMP3.1 (OUT_A), J2.2
ADC3_POS: 3R2.2, 3R5.1, 3R7.2, J2.1, X3.2, X3.3 (2), X3.4 (2), X3.5 (2)
ADC4_NEG: 8R18.1, 8R19.1, AMP4.1 (OUT_A), J2.9
ADC4_POS: 8R17.1, 8R20.2, 8R21.2, J2.8, X4.2, X4.3 (2), X4.4 (2), X4.5 (2)
ADC5_NEG: 5R3.1, 5R4.1, AMP5.1 (OUT_A), J3.2
ADC5_POS: 5R2.2, 5R5.1, 5R7.2, J3.1, X5.2, X5.3 (2), X5.4 (2), X5.5 (2)
ADC6_NEG: 8R10.1, 8R11.1, AMP6.1 (OUT_A), J3.9
ADC6_POS: 8R9.1, 8R12.2, 8R13.2, J3.8, X6.2, X6.3 (2), X6.4 (2), X6.5 (2)
ADC7_NEG: 7R3.1, 7R4.1, AMP7.1 (OUT_A), J4.2
ADC7_POS: 7R2.2, 7R5.1, 7R7.2, J4.1, X7.2, X7.3 (2), X7.4 (2), X7.5 (2)
ADC8_NEG: 8R3.1, 8R4.1, AMP8.1 (OUT_A), J4.9
ADC8_POS: 8R2.2, 8R5.1, 8R7.2, J4.8, X8.2, X8.3 (2), X8.4 (2), X8.5 (2)
GND: J6.1 (GND), J7.1 (GND), ON/OFF.3, R1.2, R2.2, R3.2
INPUT1_NEG: 1R8.1, AMP1.3 (+IN_A), X1.1
INPUT2_NEG: 8R31.1, AMP2.3 (+IN_A), X2.1
INPUT3_NEG: 3R8.1, AMP3.3 (+IN_A), X3.1
INPUT4_NEG: 8R23.1, AMP4.3 (+IN_A), X4.1
INPUT5_NEG: 5R8.1, AMP5.3 (+IN_A), X5.1
INPUT6_NEG: 8R15.1, AMP6.3 (+IN_A), X6.1
INPUT7_NEG: 7R8.1, AMP7.3 (+IN_A), X7.1
INPUT8_NEG: 8R8.1, AMP8.3 (+IN_A), X8.1
unnamed: BBB.A, J5.5
unnamed: AUX_POWER.K (C), R1.1
unnamed: J5.1, REC.A
unnamed: J5.4, ON/OFF.2
unnamed: J5.3, REC/STOP.1
unnamed: J5.2, REC/STOP.3
unnamed: R3.1, REC.K (C)
unnamed: BBB.K (C), R2.1
V+: AUX_POWER.A, F1.P$1 (1), J7.2 (V+)
V+_FUSED: F1.P$2 (2), J6.2 (V+)

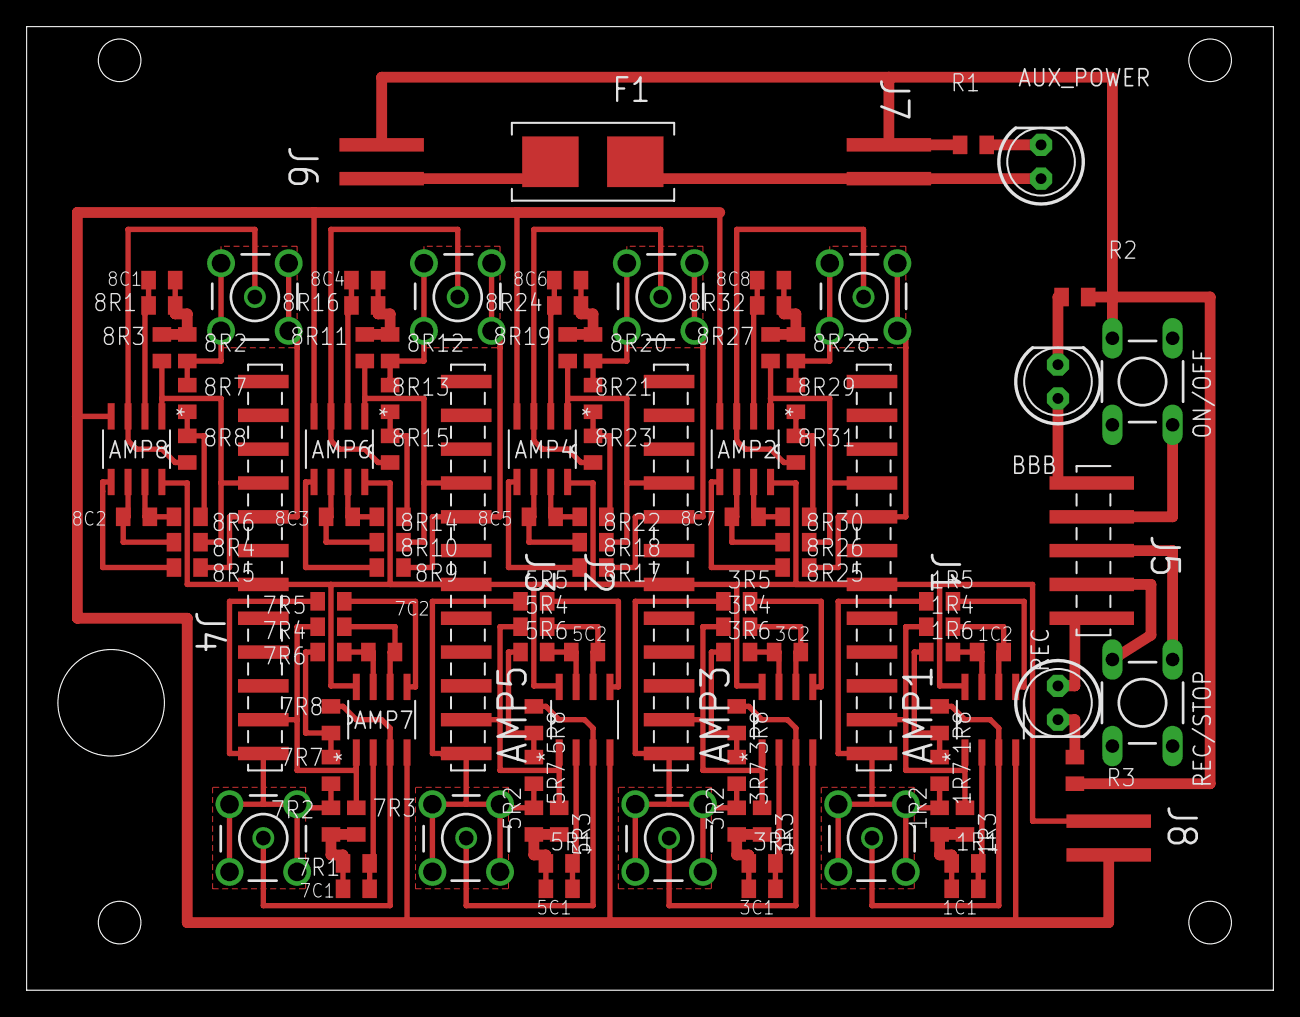
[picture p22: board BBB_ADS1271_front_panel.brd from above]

Board: 2 copper layers, 93.7 x 72.4 mm, 113 parts (0 on the bottom side), 85 nets.

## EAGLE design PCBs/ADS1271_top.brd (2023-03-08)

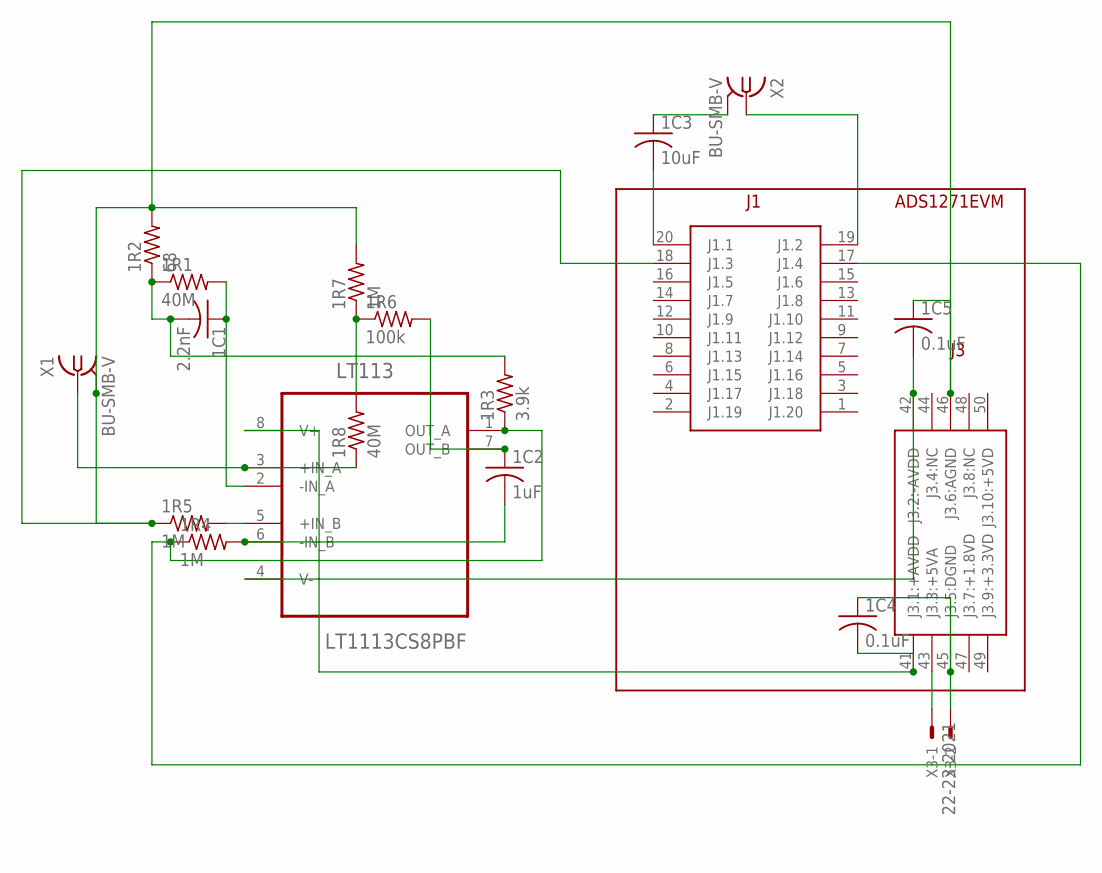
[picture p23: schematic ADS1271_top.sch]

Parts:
1C1: 2.2nF; ADAFRUIT_C0805K
1C2: 1uF; ADAFRUIT_C0805K
1C3: 10uF; ADAFRUIT_C0805K
1C4, 1C5: 0.1uF; ADAFRUIT_C0805K
1R1, 1R8: 40M; ADAFRUIT_R0805
1R2: 68; ADAFRUIT_R0805
1R3: 3.9k; ADAFRUIT_R0805
1R4, 1R5, 1R7: 1M; ADAFRUIT_R0805
1R6: 100k; ADAFRUIT_R0805
ADS1271_CONNECTORS: BENS_LIBRARY_ADS1271EVM_PART
LT113: LT1113CS8PBF; SOIC127P600X175-8N
X1, X2: BU-SMB-V
X3: 22-23-2021

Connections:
1+IN_B: 1R5.2, LT113.5 (+IN_B)
1-IN_A: 1C1.1, 1R1.2, LT113.2 (-IN_A)
1-IN_B: 1C2.2, 1R4.2, LT113.6 (-IN_B)
1OUT_B: 1C2.1, 1R6.2, LT113.7 (OUT_B)
1W1: 1C1.2, 1R1.1, 1R2.1, 1R3.2
1W2: 1R6.1, 1R7.1, 1R8.2
ADC1_NEG: 1R3.1, 1R4.1, ADS1271_CONNECTORS.17 (J1.4), LT113.1 (OUT_A)
ADC1_POS: 1C4.1, 1C5.1, 1R2.2, 1R5.1, 1R7.2, ADS1271_CONNECTORS.18 (J1.3), ADS1271_CONNECTORS.45 (J3.5:DGND), ADS1271_CONNECTORS.46 (J3.6:AGND), X1.2, X1.3 (2), X1.4 (2), X1.5 (2), X3.2
ADC2_GND: 1C3.1, X2.2, X2.3 (2), X2.4 (2), X2.5 (2)
ADC2_NEG: ADS1271_CONNECTORS.19 (J1.2), X2.1
ADC2_POS: 1C3.2, ADS1271_CONNECTORS.20 (J1.1)
INPUT1_NEG: 1R8.1, LT113.3 (+IN_A), X1.1
unnamed: ADS1271_CONNECTORS.43 (J3.3:+5VA), X3.1
unnamed: 1C5.2, ADS1271_CONNECTORS.42 (J3.2:-AVDD), LT113.4 (V-)
unnamed: 1C4.2, ADS1271_CONNECTORS.41 (J3.1:+AVDD), LT113.8 (V+)

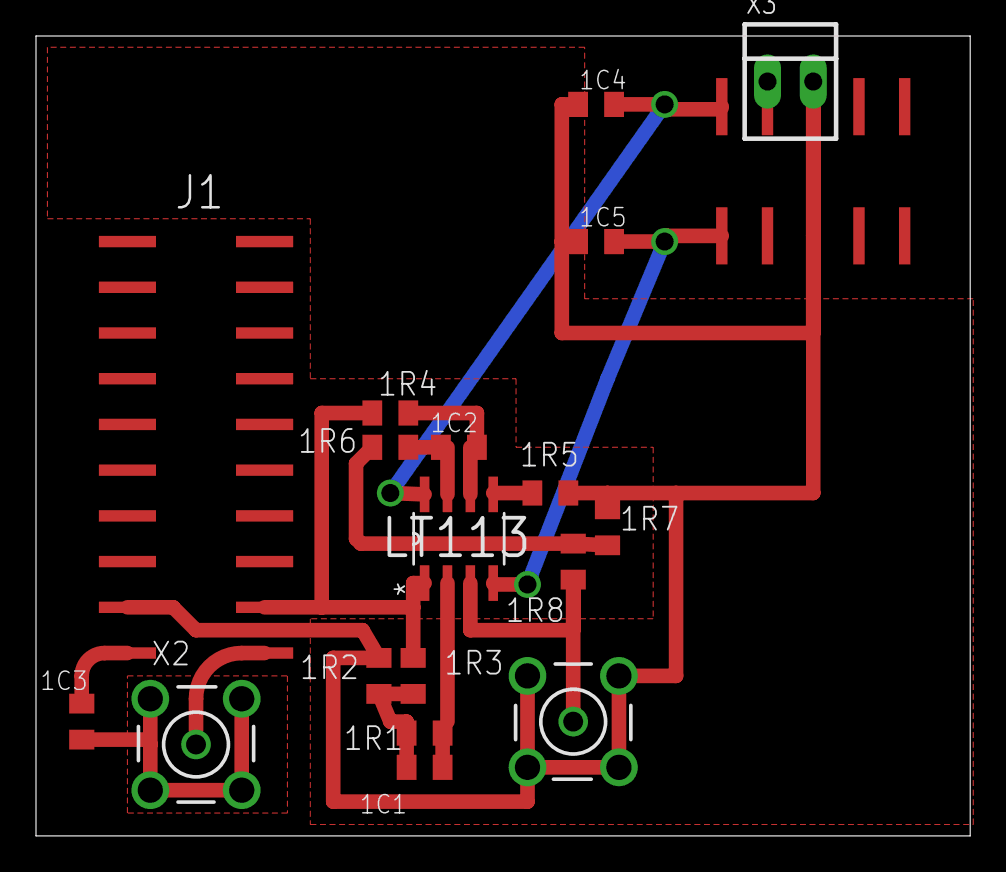
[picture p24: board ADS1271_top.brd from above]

Board: 2 copper layers, 51.9 x 44.4 mm, 18 parts (0 on the bottom side), 15 nets.

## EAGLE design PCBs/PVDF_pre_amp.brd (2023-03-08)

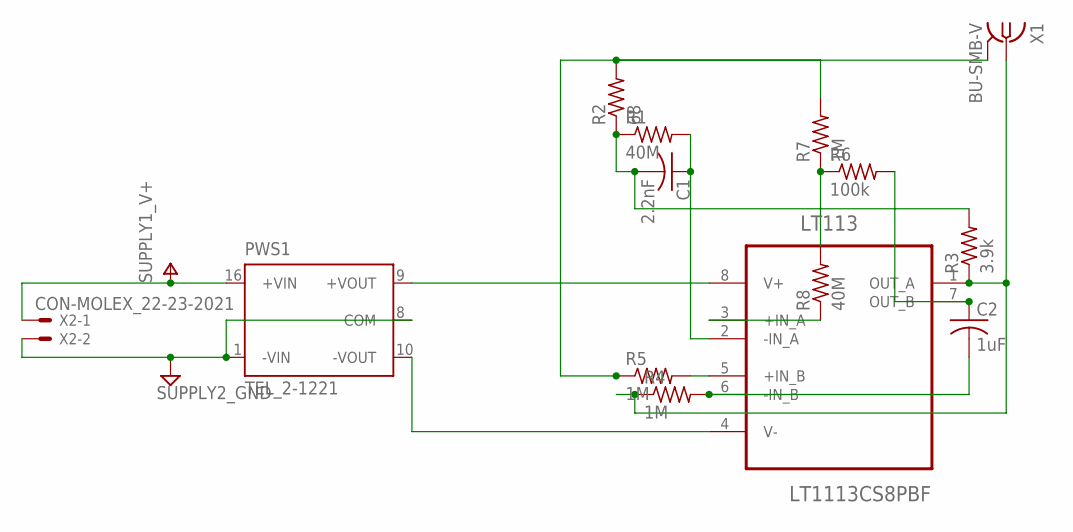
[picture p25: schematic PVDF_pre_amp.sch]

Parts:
C1: 2.2nF; ADAFRUIT_C0805K
C2: 1uF; ADAFRUIT_C0805K
LT113: LT1113CS8PBF; SOIC127P600X175-8N
PWS1: TEL_2-1221; TRACOPOWER2W
R1, R8: 40M; ADAFRUIT_R0805
R2: 68; ADAFRUIT_R0805
R3: 3.9k; ADAFRUIT_R0805
R4, R5, R7: 1M; ADAFRUIT_R0805
R6: 100k; ADAFRUIT_R0805
X1: BU-SMB-V
X2: CON-MOLEX_22-23-2021

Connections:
1+IN_B: LT113.5 (+IN_B), R5.2
1-IN_A: C1.1, LT113.2 (-IN_A), R1.2
1-IN_B: C2.2, LT113.6 (-IN_B), R4.2
1OUT_B: C2.1, LT113.7 (OUT_B), R6.2
1W1: C1.2, R1.1, R2.1, R3.2
1W2: R6.1, R7.1, R8.2
+AVDD: LT113.8 (V+), PWS1.9 (+VOUT)
-AVDD: LT113.4 (V-), PWS1.10 (-VOUT)
ADC1_NEG: LT113.1 (OUT_A), R3.1, R4.1, X1.1
GND: PWS1.1 (-VIN), PWS1.8 (COM), R2.2, R5.1, R7.2, X1.2, X1.3 (2), X1.4 (2), X1.5 (2), X2.2
INPUT1_NEG: LT113.3 (+IN_A), R8.1
V+: PWS1.16 (+VIN), X2.1

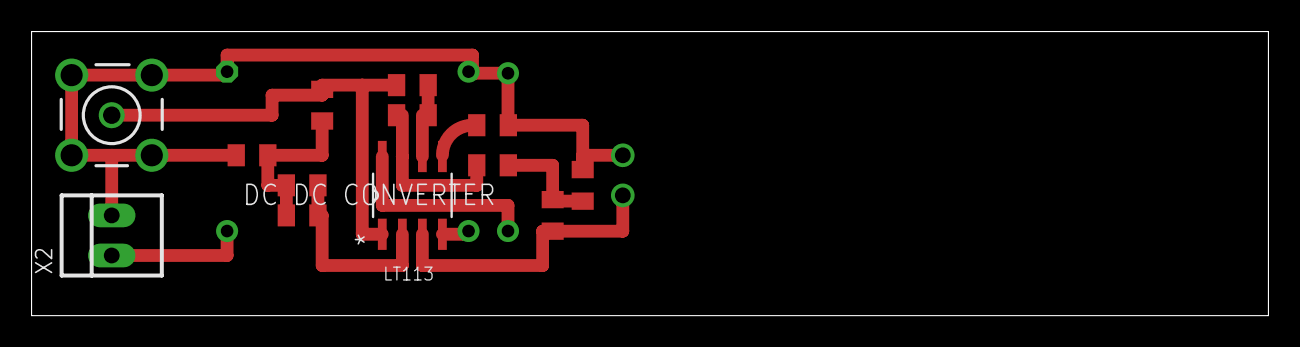
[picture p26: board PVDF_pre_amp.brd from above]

Board: 2 copper layers, 78.4 x 18.0 mm, 14 parts (1 on the bottom side), 12 nets.

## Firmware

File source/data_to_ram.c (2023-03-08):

/*
 * data_to_ram.c
 * 
 * This program uses the two PRUs on the beaglebone black to record data
 * from up to eight analog channels using four ADS1271EVMs.
 * 
 * This program is not designed to be executed directly by the user.
 * It is executed by a python helper program called "start_analysing.py"
 * 
 */

/******************************************************************************
* Include Files                                                               *
******************************************************************************/

// Standard header files
#include <stdio.h>
#include <sys/mman.h>
#include <fcntl.h>
#include <errno.h>
#include <unistd.h>
#include <string.h>
#include <linux/fs.h>
#include <stdlib.h>
#include <sched.h>
#include <complex.h>
#include <fftw3.h>
#include <time.h>
#include <math.h>
#include <sys/time.h>
#include <netdb.h>
#include <sys/socket.h>
#include <netinet/in.h>

// Driver header files
#include "prussdrv.h"
#include <pruss_intc_mapping.h>	 

/******************************************************************************
* Local Macro Declarations                                                    *
******************************************************************************/

#define BUFLEN 1400  //Max length of UDP buffer

#define PRU_NUM_0 	 0
#define PRU_NUM_1 	 1

#define DDR_BASEADDR     0x80000000
#define OFFSET_DDR	 0x00001000 

#define READY 0
#define PRU_LIMIT 10000000

//#define DEBUG

#define POWER 51 // p9.16 (EHRPWM1B) gpio1[19] corresponds to gpio51
#define PSYNC 68 // p8.10 (TIMER6) gpio2[4] corresponds to gpio68


/******************************************************************************
* Global Variable Definitions                                                 *
******************************************************************************/

// NUM_BITS - Number of bits per sample

/******************************************************************************
* Global Function Definitions                                                 *
******************************************************************************/
int set_button(int, int);

int set_button(int pin, int value)
{
	char gpio[200];

	snprintf(gpio, sizeof gpio, "%s%d%s", "/sys/class/gpio/gpio", pin, "/value");
	FILE *f = fopen( gpio, "rb+" );
	if ( f == 0 )
	{
		printf( "Could not set %s to %d\n",  gpio, value);
		fflush(stdout);
        return (-1);
	}
	fprintf(f, "%d", value);
	fclose(f);
	return 0;
}

void die(char *s)
{
    perror(s);
    exit(1);
}

int main (int argc, char **argv)
{
	//UDP stuff
	struct sockaddr_in si_me, si_other;
     
    int sock, mesg_len, slen = sizeof(si_other);
    char udp_buf[BUFLEN];	

	//create a UDP socket
    if ((sock=socket(AF_INET, SOCK_DGRAM, IPPROTO_UDP)) == -1)
    {
        die("socket");
    }
    
    char hostname[15];
    char portnum[5];
	if (argc > 5) {
		snprintf(hostname, sizeof hostname, argv[5]);
	}
	if (argc > 6) {
		snprintf(portnum, sizeof portnum, argv[6]);
	}

	struct addrinfo hints;
	memset(&hints,0,sizeof(hints));
	hints.ai_family=AF_UNSPEC;
	hints.ai_socktype=SOCK_DGRAM;
	hints.ai_protocol=0;
	hints.ai_flags=AI_ADDRCONFIG;
	struct addrinfo* res=0;
	int err=getaddrinfo(hostname,portnum,&hints,&res);
	if (err!=0) {
		die("failed to resolve remote socket address");
	}

	//Return value
	unsigned int ret = -1;
	
	// PRU/Linux Memory addresses and pointers
    void *DDR_regaddr1;
  	static int mem_fd;
	static void *ddrMem, *ERam;
	static char * ERam_char;
    unsigned int ESize, EOffs;
    tpruss_intc_initdata pruss_intc_initdata = PRUSS_INTC_INITDATA;
	const char *linux_share = "/dev/shm/bbbas";
	char pru_clock_executable[100];
	char pru_acquire_executable[100];
	
    struct timeval start, end;
	int num_seconds; // The number of seconds to be analysed
	int num_bytes = (long long)NUM_BITS/(long long)8;
	int sample_rate;
	int num_channels;
	int clk_period;
    int shift_channels = 0;
    int i;
        
	if (argc > 2) {
		sample_rate = atoi(argv[2]);
	} else {
		//Using the maximum sample rate:
		sample_rate = 130208;
	}
	switch (sample_rate) {
		case 130208 :
			clk_period = 30;
			break;
		case 97656 :
			clk_period = 40;
			break;
		case 78125 :
			clk_period = 50;
			break;
		case 65104 :
			clk_period = 60;
			break;
		case 48828 :
			clk_period = 80;
			break;
		default :
			printf("\npERROR: Please enter a valid sample rate.\n");
			fflush(stdout);
			return (ret);		
	}
    
    int fft_size = atoi(argv[3]);
		
	if (argc > 4) {
		num_channels = atoi(argv[4]);
	} else {
		//Using the maximum number of channels:
		num_channels = 8;
	}
    if (  (num_channels > 8) || (num_channels < 1) ) {
        printf("\nERROR: Please enter a valid number of channels.\n");
        fflush(stdout);
        return (ret);
    }

    if (argc > 7) {
        shift_channels = 1;
        printf("\nINFO: Channels are being shifted\n");
        fflush(stdout);
    }
    
    num_seconds = 3600; //TODO: Remove this. Setting listening time to one hour 
	if (argc > 1) {
		num_seconds = ((num_seconds) < (atoi(argv[1])) ? num_seconds : atoi(argv[1]));
	}
	
	int num_buffers = 2;
	int finished = num_buffers + 1;
	const int external_mem_size = 8388608;
	//int samples_per_buffer = (external_mem_size/num_buffers) / (num_bytes * num_channels);
	int samples_per_buffer = fft_size;
	int buffer_size = (num_bytes * num_channels) * samples_per_buffer ;
	int num_grabs = (int) ( ( (long long) num_seconds * (long long) sample_rate )/ (long long) samples_per_buffer );
    printf("INFO: Grabbing a maximum of %d seconds of data.\n",num_seconds);
    printf("INFO: Each buffer is %d bytes, which contains %d samples.\n",buffer_size, samples_per_buffer);
    printf("INFO: Each sample contains %d x %d = %d bytes.\n",num_channels,num_bytes,num_channels * num_bytes);
    printf("INFO: Grabbing %d buffers equates to %f seconds.\n",num_grabs,(float) num_grabs * (float) samples_per_buffer / (float) sample_rate);
    fflush(stdout);

    //Generate the frequency ranges
    double delta_f = (double) sample_rate / (double) fft_size;
    double centre_frequency = 1000*pow(2,(-18.)/3);
    double f_c[40];
    int f_e[41];
    int num_bands = 0;
    f_c[0] = centre_frequency;
    double upper_limit = centre_frequency*pow(2,1./6);
    f_e[0] = (int) ( centre_frequency/pow(2,1./6)/delta_f );
    f_e[1] = (int) (upper_limit/delta_f);
    while ( upper_limit < (double) sample_rate/2 ) {
        num_bands++;
        centre_frequency *= pow(2,1./3);
        upper_limit = centre_frequency*pow(2,1./6);
        if ( upper_limit >= sample_rate/2 ) { break; }
        f_c[num_bands] = centre_frequency;
        f_e[num_bands+1] = (int) (upper_limit/delta_f);
    }
    printf("  low   |  centre  |  high  | width \n"); 
    for (i = 0; i < num_bands; i++) {
        printf(" %6d | %8.2f | %6d | %8.2f\n",f_e[i],f_c[i],f_e[i+1], 0.232*f_c[i]);
    }  
    
    printf("INFO: Initialising the FFT.\n");
    fflush(stdout);
    int N = fft_size;
    double *in; 
    fftw_complex *out;
    fftw_plan p;
    in  = (double*) fftw_malloc(sizeof(double) * N);
    out = (fftw_complex*) fftw_malloc(sizeof(fftw_complex) * (N/2+1));
    p = fftw_plan_dft_r2c_1d(N, in, out, FFTW_MEASURE);
    
    double *hann;
    hann = (double*) malloc(sizeof(double )* N);
    for (i = 0; i < N; i++) { hann[i] = 0.5 * (1 - cos(2*M_PI*i/(N-1))); }
   
    printf("INFO: Opening the shared RAM for python: %s.\r\n",  linux_share);
    fflush(stdout);
	FILE *RAM_file = fopen( linux_share, "w" );
	if ( RAM_file == 0 )
	{
		printf( "Could not open the shared RAM for python\n" );
		fflush(stdout);
        return (ret);
	}

    printf("INFO: Starting the PRU/ADC program\n");
    fflush(stdout);
    /* Initialize the PRU */
    prussdrv_init ();		
    
    // Open PRU0 Interrupt
    ret = prussdrv_open(PRU_EVTOUT_0);
    if (ret)
    {
        printf("\nprussdrv_open open failed\n");
		fflush(stdout);
        return (ret);
    }
    
    // Open PRU1 Interrupt
    ret = prussdrv_open(PRU_EVTOUT_1);
    if (ret)
    {
        printf("\nprussdrv_open open failed\n");
		fflush(stdout);
        return (ret);
    }
    
    // Get the interrupt initialized
    prussdrv_pruintc_init(&pruss_intc_initdata);

    // open the device
    mem_fd = open("/dev/mem", O_RDWR | O_SYNC);
    if (mem_fd < 0) {
        printf("Failed to open /dev/mem (%s)\n", strerror(errno));
		fflush(stdout);
        return -1;
    }	

    // map the DDR memory
    ddrMem = mmap(0, 0x0FFFFFFF, PROT_WRITE | PROT_READ, MAP_SHARED, mem_fd, DDR_BASEADDR);
    if (ddrMem == NULL) {
        printf("Failed to map the device (%s)\n", strerror(errno));
		fflush(stdout);
        close(mem_fd);
        return -1;
    }
    DDR_regaddr1 = ddrMem + OFFSET_DDR;
    unsigned int *DDR_int_ptr = (unsigned int*) DDR_regaddr1;
    
 	prussdrv_map_extmem(&ERam);
 	ESize = prussdrv_extmem_size();
 	EOffs = prussdrv_get_phys_addr(ERam);
	printf("\tINFO: Size of external memory : %d\n",ESize);
    fflush(stdout);
	ERam_char = (char *) ERam;
    
    DDR_int_ptr[0] = READY; 
    DDR_int_ptr[1] = EOffs;
    DDR_int_ptr[2] = num_channels; //This int (register) holds to number of channels
    DDR_int_ptr[3] = samples_per_buffer; //This  int (register) holds the samples per buffer
    DDR_int_ptr[4] = clk_period; //This int (register) holds the clock period
    DDR_int_ptr[5] = shift_channels; //This int (register) holds the channel shift flag
    DDR_int_ptr[6] = num_buffers; //This int (register) holds the number of buffers
    
	printf("\tINFO: Initial DDR State : %d\n",DDR_int_ptr[0]);
 	printf("\tINFO: Number of channels being recorded : %d\n",DDR_int_ptr[2]);
 	printf("\tINFO: Sample per buffer: %d\n",DDR_int_ptr[3]);
 	printf("\tINFO: Sample rate: %d\n",sample_rate);
 	printf("\tINFO: Clock period (ns): %d\n",DDR_int_ptr[4]);
    fflush(stdout);

	// Set the POWER line to high
    printf("\tINFO: Powering up the ADCs\r\n");
    fflush(stdout);
    set_button(POWER,1);
	
	// Wait for ADC to settle
	usleep(500000);

    // Start the clock running on PRU1
	snprintf(pru_clock_executable, sizeof pru_clock_executable, "./prucode_clk.bin");
	printf("\tINFO: Executing the clock %s code on PRU1.\r\n",pru_clock_executable);
    fflush(stdout);
	prussdrv_exec_program (PRU_NUM_1, pru_clock_executable);

	// Set the PSYNC line to high
    printf("\tINFO: Turning on the ADCs\r\n");
    fflush(stdout);
    set_button(PSYNC,1);
	
	// Wait for ADC to settle
	usleep(10000);

    // Start recording data on PRU0 
	snprintf(pru_acquire_executable, sizeof pru_acquire_executable, "./prucode_%d.bin", clk_period);
    printf("\tINFO: Executing data gathering code %s on PRU0.\r\n",pru_acquire_executable);
    fflush(stdout);
    prussdrv_exec_program (PRU_NUM_0, pru_acquire_executable);

	struct sched_param param;
	param.sched_priority = 98;
	if (sched_setscheduler(0, SCHED_FIFO,& param) == 0 )
		{
		printf("\tINFO: data_to_ram program has maximum priority\n");
		fflush(stdout);			
		}
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
